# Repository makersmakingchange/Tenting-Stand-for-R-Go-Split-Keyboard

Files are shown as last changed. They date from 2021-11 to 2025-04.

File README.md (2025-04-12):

# Tenting Stand for R Go Split Keyboard
A low profile stand that allows for varying the angle of the R-Go Split Keyboard.

The Tenting Stand is a fully 3D printed device that allows an R-Go Split Break Ergonomic Keyboard to be supported at 5 different tenting angles. A tenting angle can help reduce pronation of the forearm and improve ergonomics. Using this stand, the user can elevate their keyboard at a 0, 5, 10, 14, or 15-degree angle.

## Usage

The user can move the legs to whichever angle is best suited to them using the tabs protruding from the front. The stand will then lock into place. When finished, the user can lower the stand back to 0 degrees and leave each half separated, or push them back together.

## Required Skills

- 3D printing
- Pulling (for cable ties)
- Pinching (for assembling legs to clips)

## Required Components

- 4x - 4" cable ties (https://www.leevalley.com/en-ca/shop/home/storage/ties/58888-standard-cable-ties?item=03K7010)
- 1  - Sheet of Adhesive-Backed Craft Foam (https://canada.michaels.com/en/9x12-adhesive-foam-sheet-by-creatology/M10032002.html?dwvar_M10032002_color=Black)

## Printing Instructions

- Print the STL files in their given orientations
- 0.2 mm Layer height
- No supports
- No brim

## Build Instructions

This device consists of several 3D printed components, zip ties, and a sheet of craft foam. Alternatively, some other non-slip sheet of material can be used in place of the craft foam. All STL’s and documentation can be found in the downloadable maker files in the GitHub Repository.

<!-- ABOUT MMC START -->
## About Makers Making Change
[Makers Making Change Logo](https://www.makersmakingchange.com/)

Makers Making Change is a program of [Neil Squire](https://www.neilsquire.ca/), a Canadian non-profit that uses technology, knowledge, and passion to empower people with disabilities.

Makers Making Change leverages the capacity of community based Makers, Disability Professionals and Volunteers to develop and deliver affordable Open Source Assistive Technologies.

 - Website: [www.MakersMakingChange.com](https://www.makersmakingchange.com/)
 - GitHub: [makersmakingchange](https://github.com/makersmakingchange)
 - Bluesky: [@makersmakingchange.bsky.social](https://bsky.app/profile/makersmakingchange.bsky.social)
 - Instagram: [@makersmakingchange](https://www.instagram.com/makersmakingchange)
 - Facebook: [makersmakechange](https://www.facebook.com/makersmakechange)
 - LinkedIn: [Neil Squire Society](https://www.linkedin.com/company/neil-squire-society/)
 - Thingiverse: [makersmakingchange](https://www.thingiverse.com/makersmakingchange/about)
 - Printables: [MakersMakingChange](https://www.printables.com/@MakersMakingChange)

### Contact Us
For technical questions, to get involved, or to share your experience we encourage you to [visit our website](https://www.makersmakingchange.com/) or [contact us](https://www.makersmakingchange.com/s/contact).
<!-- ABOUT MMC END -->

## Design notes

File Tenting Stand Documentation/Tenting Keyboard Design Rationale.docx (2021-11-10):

# Background

There are two commercially available ergonomic keyboards that are split into two parts to make it easier to position them. One of the keyboards is available with an accessory that provides adjustable tenting angles, which can reduce the forearm pronation caused by flat keyboards. The purpose of this project was to create a similar accessory for the keyboard that doesn’t have an adjustable tenting angle accessory.

# Requirements

- The device should be able to put the R-Go Split keyboard into a tented angled orientation when split into two parts.
- The keyboard can be set to tenting angles of 5, 10, and 15 degrees.
- User should be able to easily adjust angles and remove device to use keyboard flat.
- When in use, keyboard should be stable.

# Research

## Existing Designs

The R-Go Split Ergonomic Keyboard (https://www.r-go-tools.com/products/ergonomic-keyboards/r-go-split/qwerty-us-black-wired/ , $https://www.r-go-tools.com/products/ergonomic-keyboards/r-go-split/) is commonly recommended by the AT specialists within Neil Squire Solutions for clients. It is very thin, and because it is split, each hand can be positioned in an optimal position. It also requires very little force to depress the keys.

The Kinesis Freestyle2 Split Ergonomic Keyboard (https://kinesis-ergo.com/shop/freestyle2-for-pc-us/, $99 USD) is another split keyboard. It has an optional accessory for tenting called the Freestyle2 V3 (https://kinesis-ergo.com/shop/freestyle2-v3-accessory/, $26.95 USD).

# Initial Design – V1.0

The initial design was heavily based on the Kinesis Freestyle2 V3 Tenting Accessory and modified to be compatible with the R-Go Split Ergonomic Keyboard and designed to be 3D printed instead of injection molded.

This design consists of three main bodies: a clip, a short arm, and a long arm. The clip attaches to the R-Go Keyboard. The short and long arms attach to the clip. The tenting stand provides a 5-degree tenting angle when both arm are open. The short arm and long arm can then be attached together to provide the other tenting angles. It provides a 10-degree angle in one position, and a 15-degree angle in the other position. The arms consist of multiple bodies that are glues together to provide flat surfaces for quick printing without needing support.

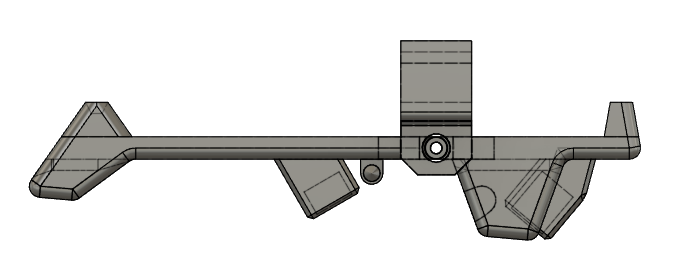
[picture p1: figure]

Figure 1: Initial Design – 5-degree Configuration

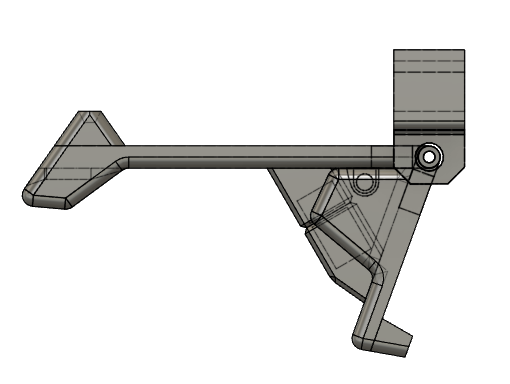
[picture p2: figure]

Figure 2: Initial Design – 10-degree Configuration

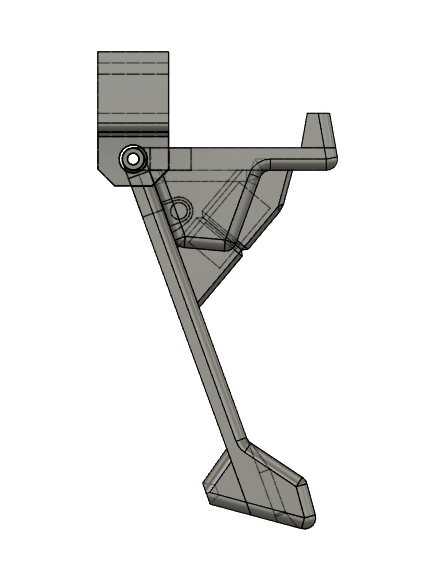
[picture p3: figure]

Figure 3: Initial Design - 15-degree Configuration

## Arm Attachment

The original design uses a snap-fit clip to attach the two arms together. We attempted to use a 3d printer compatible snap-fit into this design, but were limited by the available space and managing the strength/durability related to print direction.

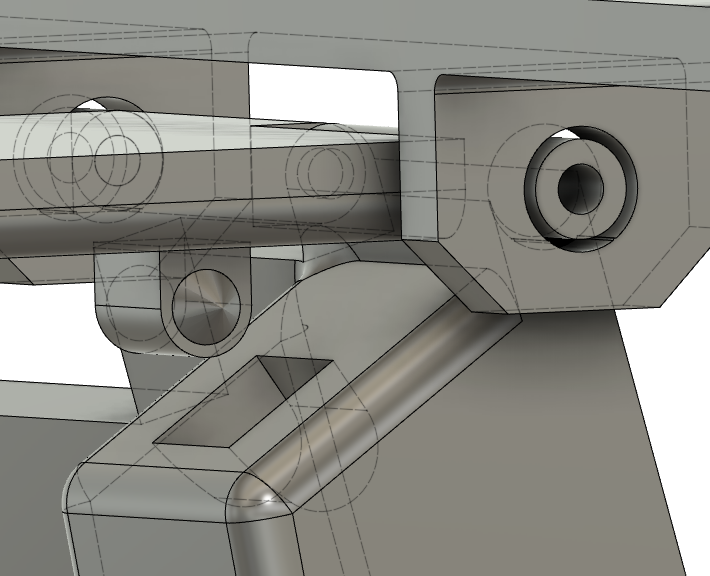
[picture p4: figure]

Figure 4: Initial Snap Fit Design

As an alternative, a design incorporating magnets was used to provide some locking force for the arms. The limited space available based on the geometry between the different configuration of the arms limited the size and number of magnets that could be used. The magnets were inserted within 3d printed components by pausing the print and super glued into place. This technique worked, but there are several drawback. First, not all printers are able to easily pause prints to allow the magnets to be inserted. Second, the method requires manual intervention during the printing process and is prone to error (i.e., the magnets must be installed with correct polarity).

## Opportunities for Improvements

Function - Arm Attachment Mechanism

Initial snap fit didn’t work reliably and wear away after a small number of uses. Magnets don’t provide enough locking force.

Assembly

Assembling the arms into the clips is difficult, as the pins are in different directions and requires the clip to be bent and contorted.

The arms consist of multiple components that need to be superglued into place.

Stiffness/Durability

Don’t have much feedback on the devices that have been created and in use, but unsure if they will stand up to rough usage.

Clip is too small. The portion of the clip that has the hole for the arm’s pin is too small.

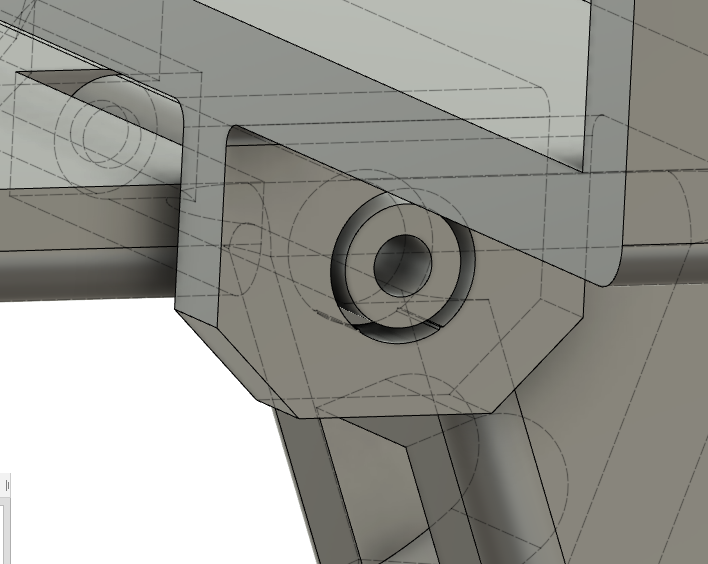
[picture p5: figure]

Figure 5: Area of Clip That Is Too Thin

## Improving Existing Components

Clip: Use the same clip, as it works, but add a small hole in the centre for a printed pin insert to spread the hinge pins into place.

Arms: Fill in the empty space on the side with the smaller foot so they can be printed as one piece. Arrange pins to face the same direction and add space for the pin.

# Version 2 - Ideation

The proposed device features a toothed locking mechanism conceptualised from an old beach chair ratcheting mechanism, or similarly, the locking mechanism on an ironing board.

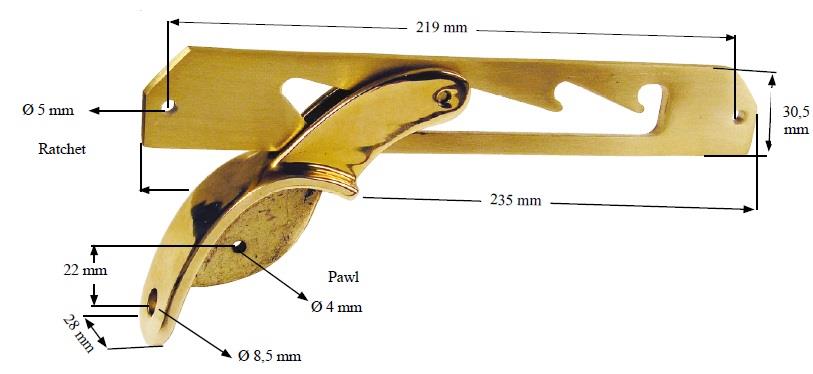
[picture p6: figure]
Beach chair reclining arm mechanism - Woodworking Stack Exchange

## Ideation of components

Clip: The clip onto the keyboard the current design features works well. This can be implemented into the new design, but extending it out to hold the entire keyboard, and moving the hinges to the side. This clip will have a hinge on one end to attach to the base, and legs on the other end.

Legs: The height of the legs is determined through the max angle of 15 degrees, where the legs will be perpendicular with the base. Originally the legs were two separate pieces with snap fits to hold them on, but joining them into one piece allows them to move as one, making the device more use friendly. Joining them also allows them to hold onto the clip by their own rigidity. The legs are triangular so the ‘foot’ will be able to lock into the ridges easier at narrow angles.

Base: The base features ridges for the legs to rest on to create different angle, and a hinge for the clip to fit into. To secure the clip to the base, there are notches under the base for zip ties or string to wrap around the entire hinge.

# Version 3 – Ideation

This design resulted from a meeting with Jake on the previous two designs. It functions intermediately to the two designs and features a clip on base, with two sets of legs that attach at a hinge. When folded down, the legs put the keyboard on a 5 degree angle, and 10 or 15 degrees when either of the legs is folded out.

# Prototyping

Version 1:

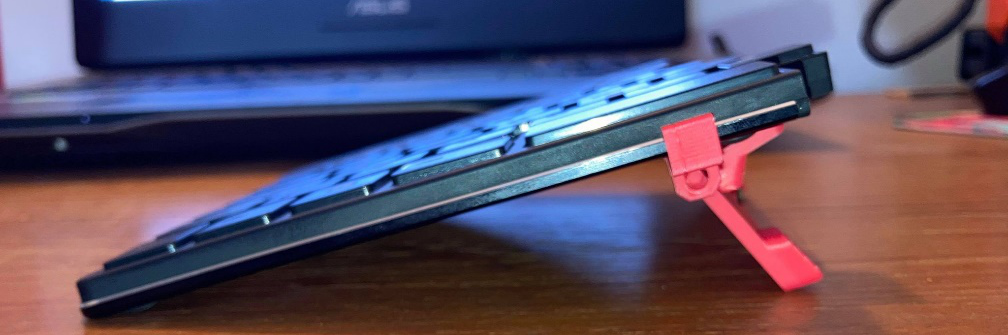
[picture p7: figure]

Version 2:

Version 3:

# Final Design Selection

The following chart shows the key elements of each design and ranks them as either better or worse than the other.

Design | Print Complexity | Print Time | Assembly Complexity | Stability | Compactness | Adjustability | Ease of Locking into/out of Position
V1 | Worse | Better | Worse | | Better | Worse | Worse
V2 | | Worse | Medium | | Worse | Better | Better
V3 | | Medium | Better | | Medium | Medium | Better

Based off feedback from OT’s with Solutions, the Version 2 (ratchet concept) stand was selected.

Changes made to the Final Design:

To improve the stability of the stand at angles, the interface between the legs and base are a rounded leg and a series of “cups” on the base the legs fit into. A tab was also added to the legs for easier adjustment of the stand.

Craft foam was used to cover the bottom of the base to reduce slipping along the surface when typing.

The inner edge profile of each base was modified to provide support to the parts of the keyboard halves that extend further into the middle, while also being able to nest together closely.

Due to the different lengths of each keyboard half, when tented with the outer edge as the fulcrum point, the inner edges of the keyboards are at different heights. At higher tenting angles, this is increasingly noticeable. This can cause discomfort in use as it might cause someone to sit with their shoulders at different angles to compensate, it also may reduce rejection of the device.

# Opportunities for Improvement

Ratchet: Size reduction

# Credited Resources Used In Development

1 R-Go split Keyboard

© 2021 by Neil Squire. This work is licensed under the CC BY SA 4.0 License: http://creativecommons.org/licenses/by-sa/4.0 Files available at Page 3 of 6

V2.0 | July 2021 Tented Stand for R-Go Split Keyboard Design rationale

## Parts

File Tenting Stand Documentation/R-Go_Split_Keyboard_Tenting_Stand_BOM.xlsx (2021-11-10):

Device: R-Go Split Keyboard Tenting Stand |  | Total Cost | Total Print time (hr) | Total filament (g)
Version: V2.0 | Date Created: 4/20/2021 | $4.11 | 0.00 | 101.12
Commercial Parts:
Part type (Electrical. Mechanical, Sanitization, ect) | Part Name | Quantity Needed | Pkg Quantity | Price per package | Price per Unit | Price for qty needed | Link
Mechanical | Craft Foam Sheet | 1 | 1 | $1.49 | $1.49 | $1.49 | https://canada.michaels.com/en/9x12-adhesive-foam-sheet-by-creatology/M10032002.html?dwvar_M10032002_color=Black
Mechanical | Zip Ties | 4 | 100 | $2.20 | $0.02 | $0.09 | https://www.leevalley.com/en-ca/shop/home/storage/ties/58888-standard-cable-ties?item=03K7010
3D Printed Parts ESTIMATED PRICING USING 1KG ROLL COST: | $25.00
Part | Description | Quantity Needed | TOTAL Mass (g) | Estimated Price | Print Time (Min) | Link
Left Base |  | 1 | 28.29 | $0.71
Right Base |  | 1 | 28.88 | $0.72
Left Clip |  | 1 | 17.45 | $0.44
Right Clip |  | 1 | 13.26 | $0.33
Left Legs |  | 1 | 6.4 | $0.16
Right Legs |  | 1 | 6.84 | $0.17
 |  |  | Total Print Cost: | $2.53
Tools for Assembly
Exacto knife/scissors
Alternatives (if there are other sources for some parts link them below)
Part and description | Link
Dycem | https://www.amazon.ca/Dycem-Non-Slip-Material-Roll-Blue/dp/B000C23XJG?hvadid=292923720702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

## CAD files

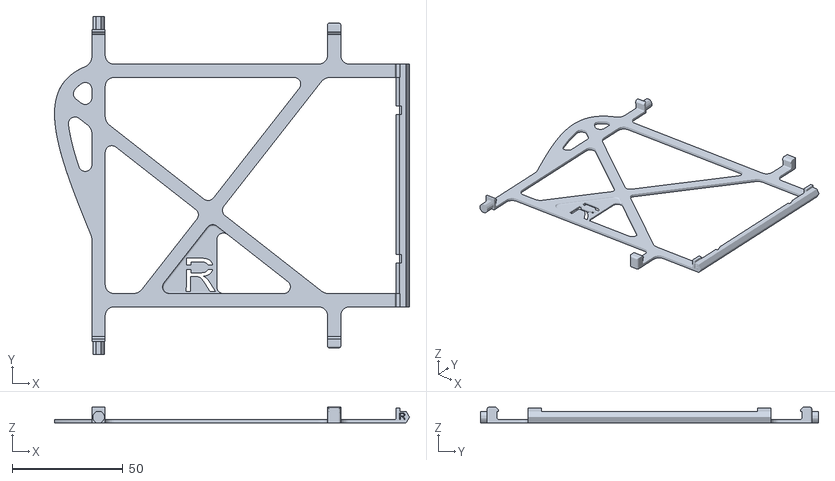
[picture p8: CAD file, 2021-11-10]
Tenting Stand STLs/Tenting Stand Right Clip.stl
160.2 x 152.7 x 7.10

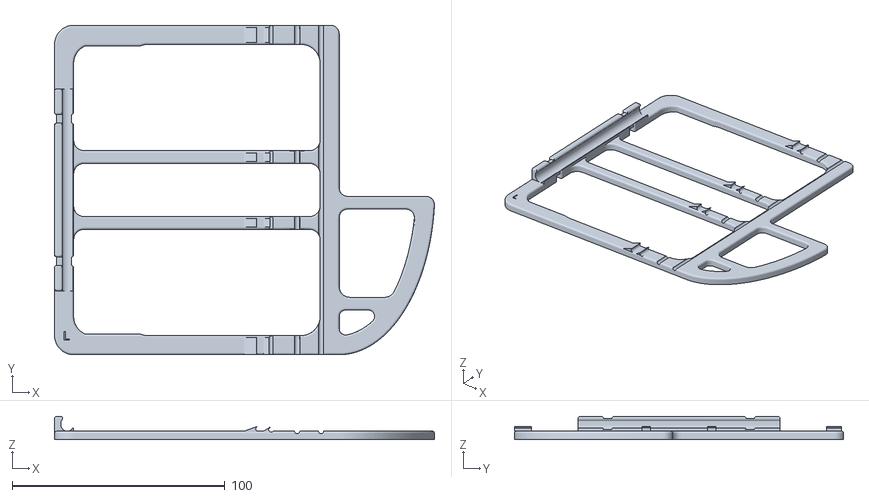
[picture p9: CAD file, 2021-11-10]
Tenting Stand STLs/Tenting Stand Left Base.stl
178.8 x 155.0 x 11.0

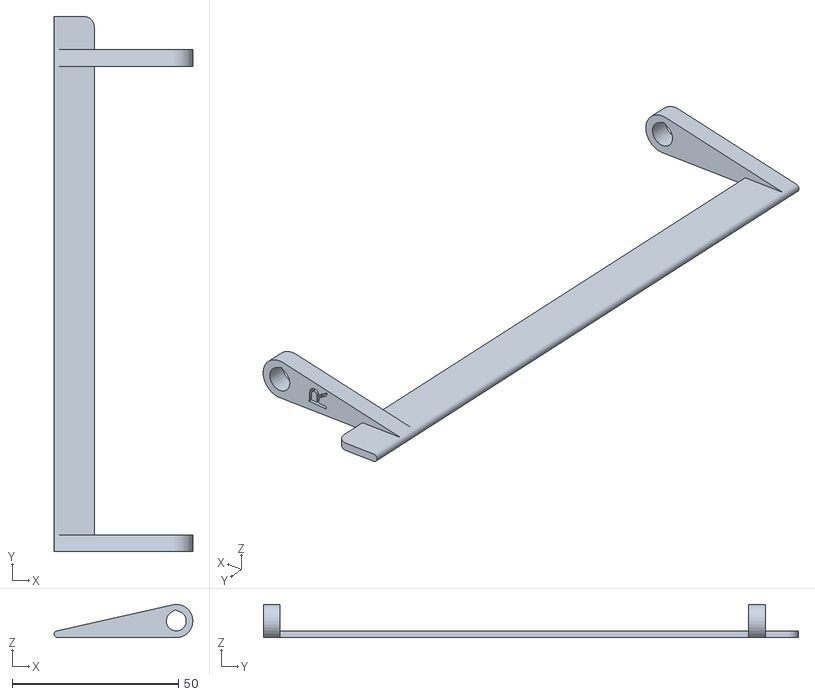
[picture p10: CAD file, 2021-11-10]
Tenting Stand STLs/Tenting Stand Right Legs.stl
41.8 x 161.0 x 9.95

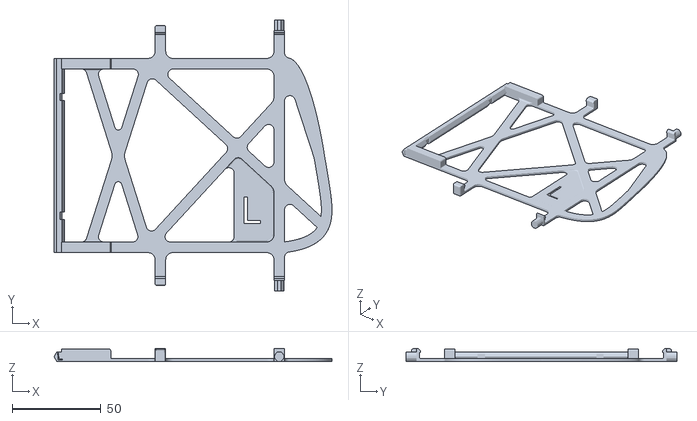
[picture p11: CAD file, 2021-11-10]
Tenting Stand STLs/Tenting Stand Left Clip.stl
156.7 x 152.7 x 7.10

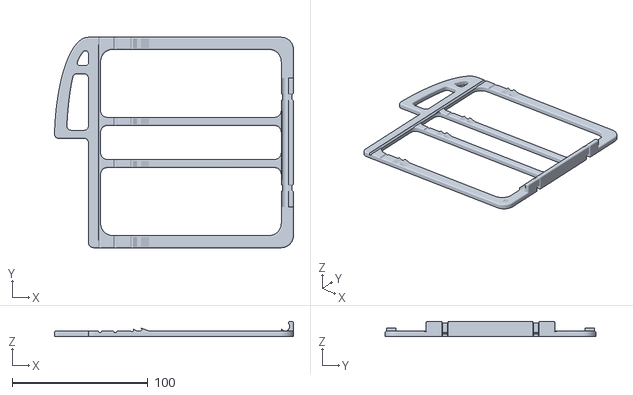
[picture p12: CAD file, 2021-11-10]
Tenting Stand STLs/Tenting Stand Right Base.stl
175.9 x 155.0 x 11.0

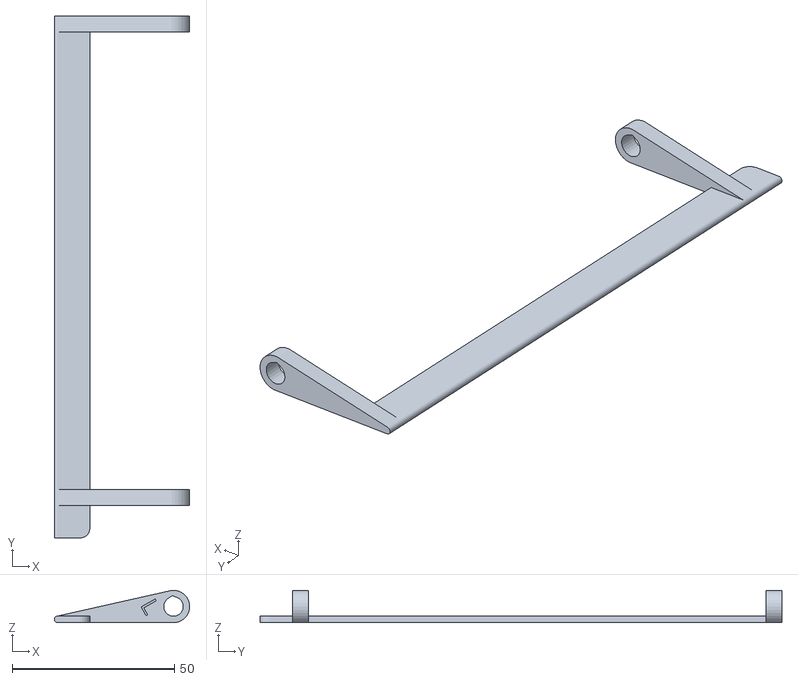
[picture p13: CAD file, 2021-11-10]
Tenting Stand STLs/Tenting Stand Left Legs.stl
41.8 x 161.0 x 9.95

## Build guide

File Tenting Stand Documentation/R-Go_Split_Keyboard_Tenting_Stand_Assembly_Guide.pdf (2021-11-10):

# Assembly Guide Device: R-Go Split Keyboard Tenting Stand

### Version: 2.0 Date: 09/21/2021

## Components needed:

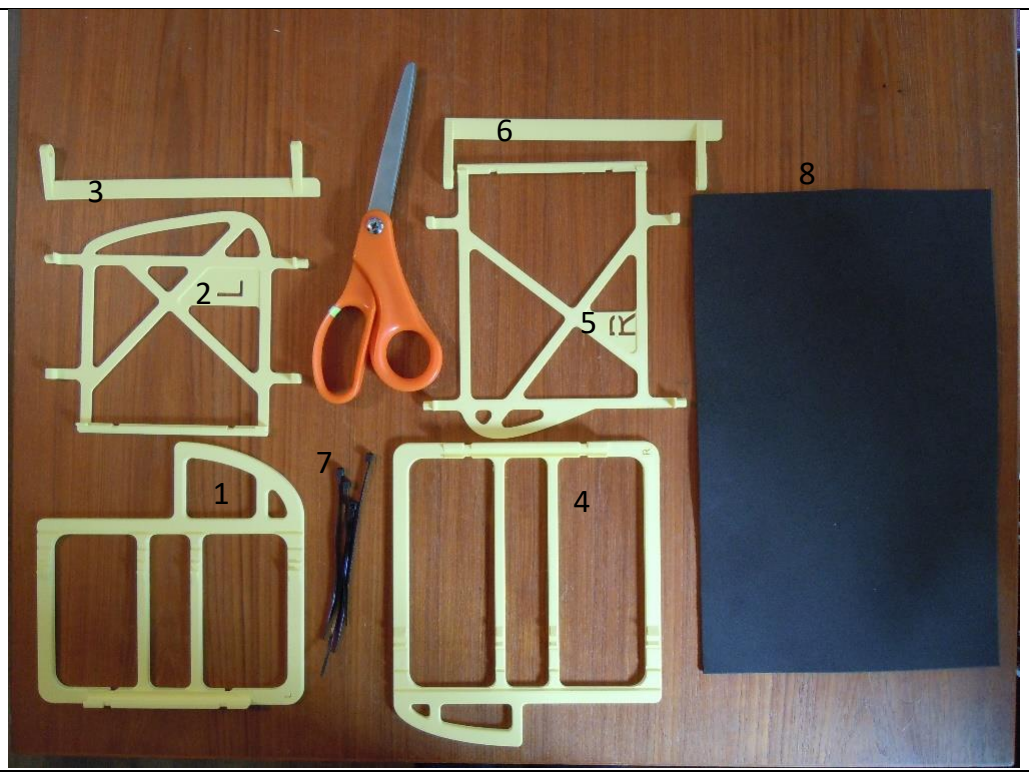
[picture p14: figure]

## BOM

### 1. Left Base 2. Left Clip 3. Left Legs 4. Right Base 5. Right Clip 6. Right Legs 7. 4 Zip Ties 8. Craft Foam/Dysom

## TOOLS NEEDED:

- Sharp blade/scissors

# Step 1:

Description: 3D print the STL models of the stand. One of each piece is required, and all models are in the proper print orientation. Print settings are 0.2mm layer height, and no supports or brim.

# Step 2:

Description: Attach the leg pieces to their corresponding clips. Ensuring the leg tab lines up with the label of the clip and that the flat portion connecting the two legs is underneath the clip, insert one protruding octagonal shaft into the leg hole and then flex the clip to insert the other side.

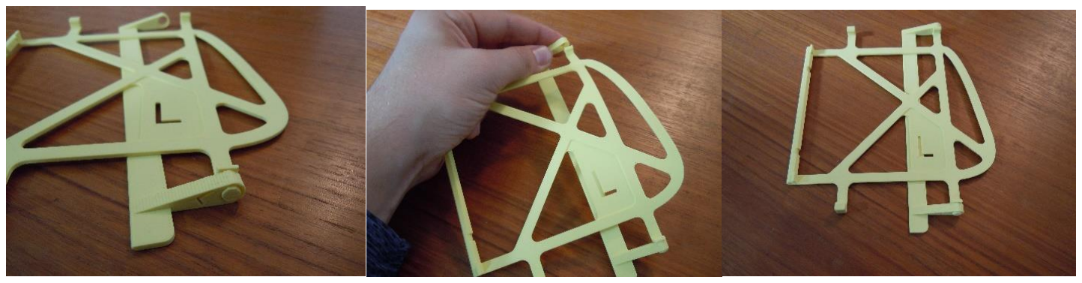
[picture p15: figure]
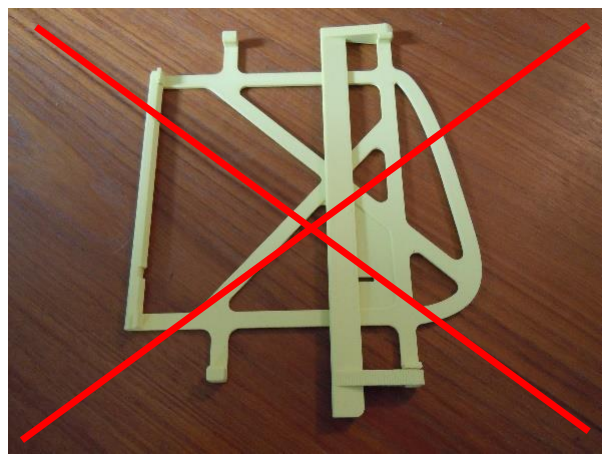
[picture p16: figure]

# Step 3:

Description: Attach the clips to their corresponding bases. Ensure the fully flat side of each piece faces down and place the hexagonal shaft into the open hinge on the base. Line up the vertically cut out sections and secure in these spots with a zip tie wrapped around. Ensure to line up the zip tie as shown in the photos, that is, with the ‘head’ of the zip tie pointing updwards. Cut off the excess end of the zip tie and tuck the head of it to the inside to the stand.

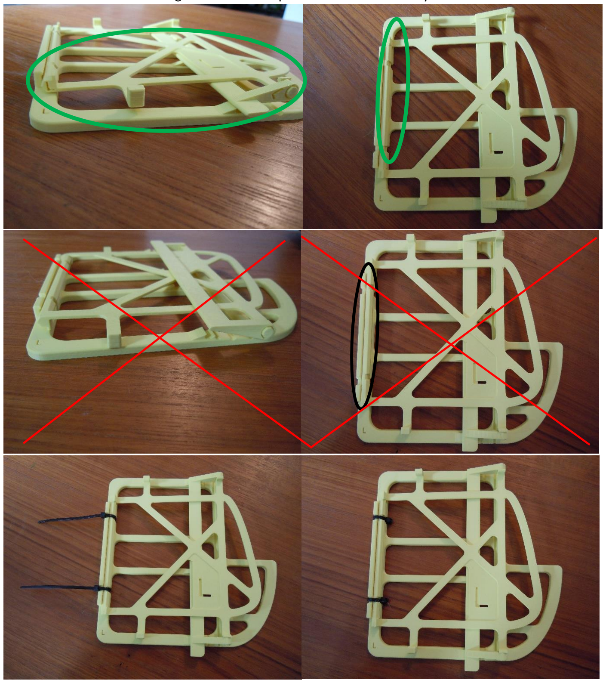
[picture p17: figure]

Note: You can use some string or twist ties if zip ties are unavailable to you.

# Step 4:

Description: Cut approximately 6mm wide strips of foam to adhere onto the bottom of the bases. You should ideally cover at least each outside corner on the base (5 total per base).

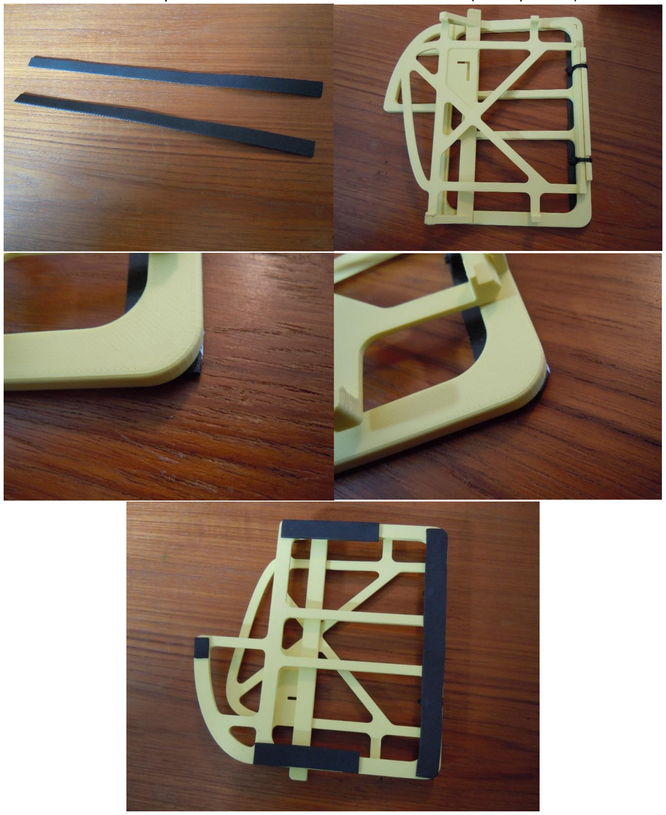
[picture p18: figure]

# Step 5:

Description: Clip in the keyboard halves into their respective stands. The interfacing sections of the keyboard should face in towards each other when inserted properly. The footprint of the keyboard halves should roughly match that of the piece they are inserted into.

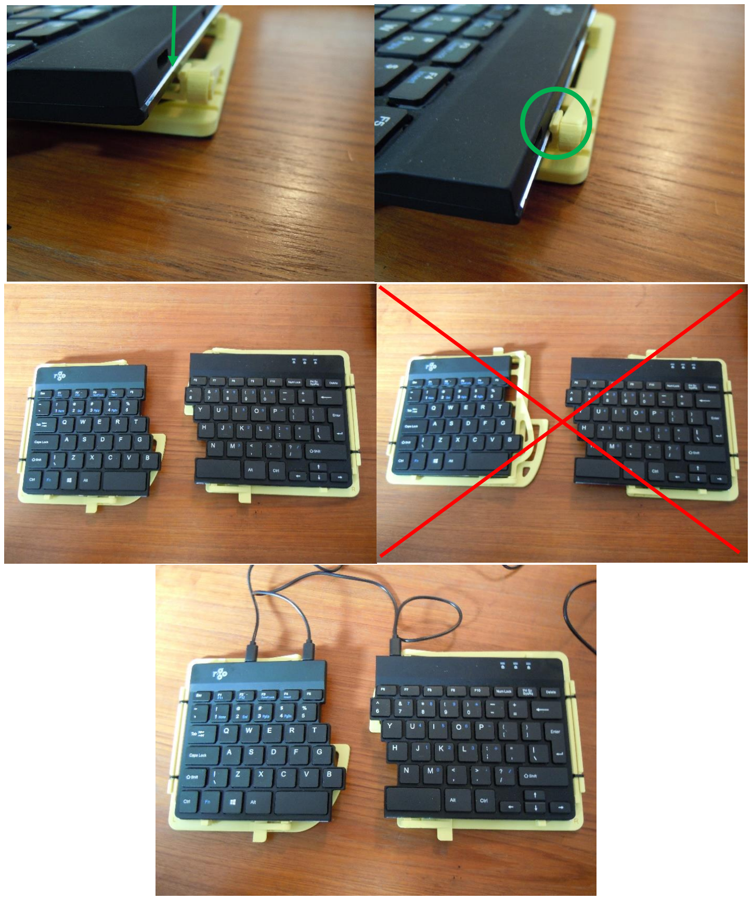
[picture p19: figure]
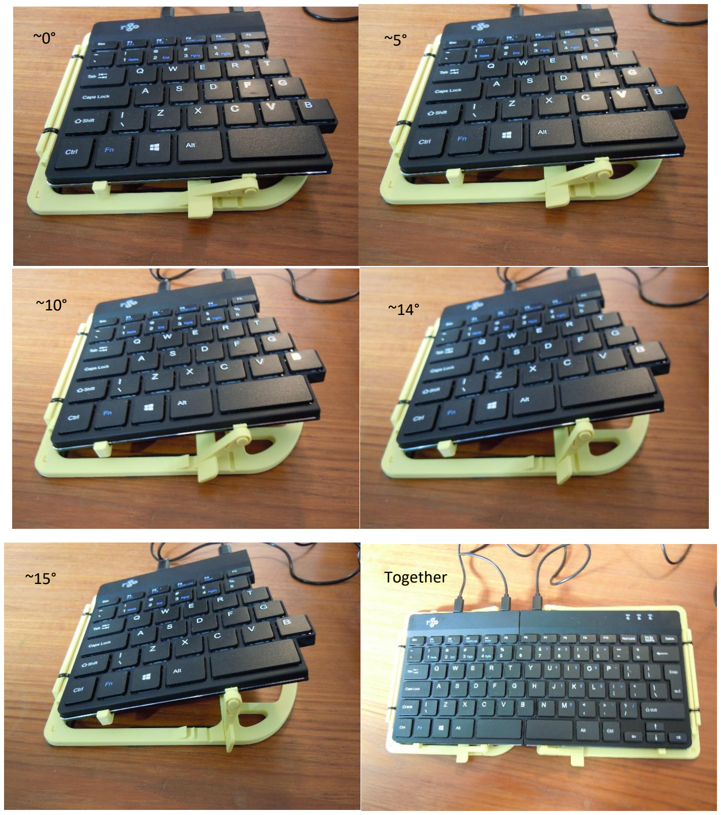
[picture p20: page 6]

~0° | ~5°
~10° | ~14°
~15° | Together
